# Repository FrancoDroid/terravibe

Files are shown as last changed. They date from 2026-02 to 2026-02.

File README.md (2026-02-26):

# Terra Vibe - Peneira Vibratória
No campo da arqueologia, muitos processos ainda dependem de ferramentas manuais que, embora eficientes, podem tornar o trabalho repetitivo, demorado e suscetível a variações humanas. A peneiração de sedimentos é um desses processos: essencial para identificar artefatos e microvestígios, mas frequentemente limitada por equipamentos improvisados ou difíceis de transportar.

Este projeto nasceu da necessidade de criar uma solução acessível, portátil e replicável para equipes de campo e laboratórios: uma peneira vibratória open source, com componentes de baixo custo. O objetivo é acelerar o processo, reduzir o esforço físico, melhorar a eficiência da triagem e aumentar a confiabilidade dos resultados.

A proposta permite que qualquer grupo possa construir, adaptar ou otimizar o equipamento de acordo com suas necessidades específicas. Ao tornar o projeto open source, pretendemos facilitar a colaboração entre arqueólogos, pesquisadores e desenvolvedores, promovendo melhorias contínuas e ampliando o acesso a ferramentas profissionais de peneiração.

Gemini_Generated_Image_eo8nz3eo8nz3eo8n

## Fatores Principais

- Completamente gratuito e open source
- Estrutura fixa e resistente a base de canos PVC
- Não requer microcontroladores ou hardwares caros
- Possui ajuste de velocidade de peneiração para agilidade ou para fragmentos mais fragéis.
- Componentes acessíveis e fáceis de obter
- Não requer instalação de software/circuitos elaborados
- Funcionamento requer apenas uma tomada de 110v

## Como Funciona?

O processo é simples: o usuário distribui o material a ser peneirado (solo, sedimentos ou fragmentos arqueológicos) sobre a superfície da peneira, garantindo que esteja espalhado de forma uniforme. Logo abaixo da peneira, posiciona-se um recipiente de coleta, como um balde ou bandeja, que irá receber a terra, areia ou outros materiais indesejados que passarem pela malha durante o processo. Em seguida, com o TerraVibe ligado a tomada, basta ajustar o potenciômetro para definir a intensidade de vibração desejada. Essa vibração facilita a separação natural dos fragmentos: pedaços maiores (como artefatos, fragmentos cerâmicos ou pequenas estruturas) permanecem sobre a peneira para análise enquanto, os materiais indesejados caem para o recipiente de coleta através da malha.

## Lista de Materiais

| Componente                              | Quantidade | Preço Unidade (R$) | Preço (R$) |
|-----------------------------------------|------------|----------------------|------------|
| Joelho 90 PVC 25mm                      | 4          | 0,58                 | 2,32       |
| Tê PVC 25mm                             | 6          | 0,99                 | 3,96       |
| Luva PVC 25mm                           | 1          | 0,64                 | 0,64       |
| Conexão Tubo Curva 3 Saídas PVC 25 mm   | 4          | 6,29                 | 25,16      |
| Peneira 60x40cm                         | 1          | 59,90                | 59,90      |
| Molas de Tração                         | 4          | 9,50                 | 38,00      |
| Corda Elástica com Gancho               | 1          | 21,13                | 21,13      |
| Cano PVC 20mm (3 metros)                | 3          | 9,50                 | 28,50      |
| Cano PVC 20mm (1 metro)                 | 1          | 5,65                 | 5,65       |
| Cabo Elétrico 1 metro 1,5mm²            | 1          | 3,23                 | 3,23       |
| Controlador p/ Motor                    | 1          | 17,52                | 17,52      |
| Motor                                   | 1          | 42,95                | 42,95      |
| Fonte Bivolt 12V 50A DC                 | 1          | 96,45                | 96,45      |
| Cabo Extensor Acendedor                 | 1          | 2,66                 | 2,66       |
| Fusível 15A 250V                        | 1          | 0,97                 | 0,97       |
| Plugue de tomada (2 pinos)              | 1          | 2,89                 | 2,89       |
| Total                                   | —          | —                    | 351,93     |

## Manual de Montagem

Nós montamos o nosso TerraVibe de uma forma e documentamos ela em um guia de montagem com o passo-a-passo para produção. A baixo, temos o link do manual.

(https://github.com/FrancoDroid/terravibe/blob/main/Manual%20de%20Montagem%20-%20TerraVibe.pdf)
## Imagem da TerraVibe

A TerraVibe é a nossa solução portátil em cano de PVC. A estrutura é leve e a peneira tem 30 por 60 centímetros. O sistema usa um motor alimentado por fonte e controlado por um potênciometro que permite ajustar a intensidade da vibração. Isso garante que a terra seja separada sem danificar os artefatos. 

Foto de Miguel López

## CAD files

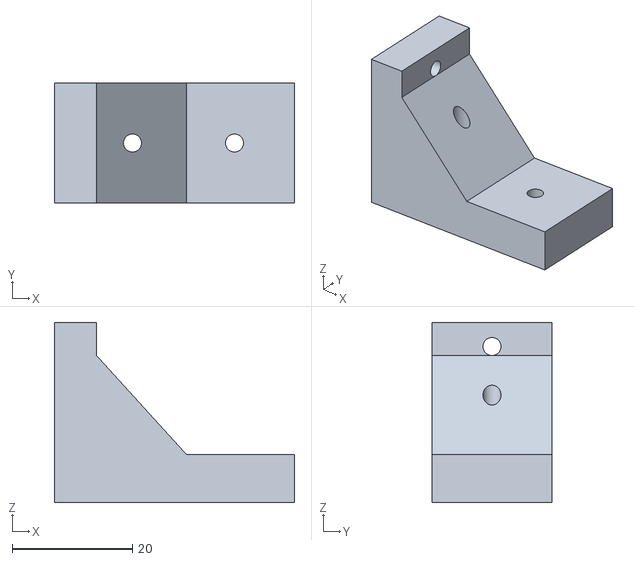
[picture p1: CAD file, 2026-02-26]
Peças para Impressão 3D/cantoneira peneira 2.STL
40.0 x 20.0 x 30.0

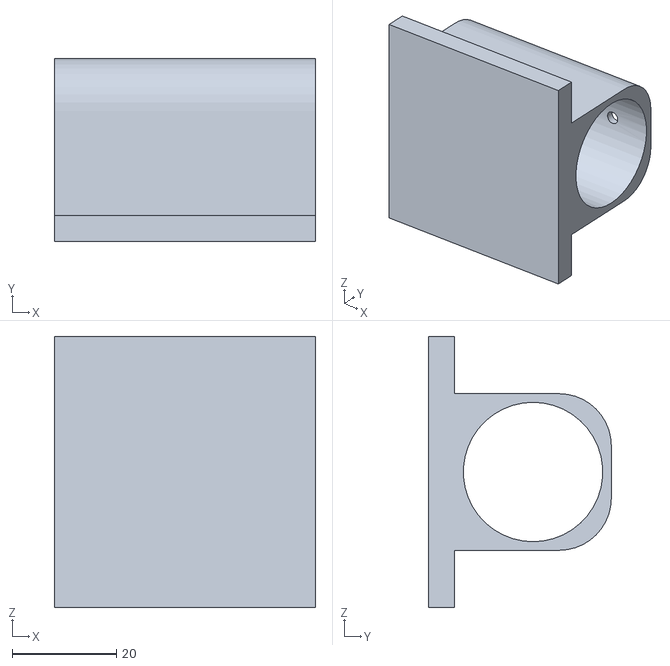
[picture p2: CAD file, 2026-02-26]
Peças para Impressão 3D/abraçadeira.STL
50.0 x 35.0 x 52.0

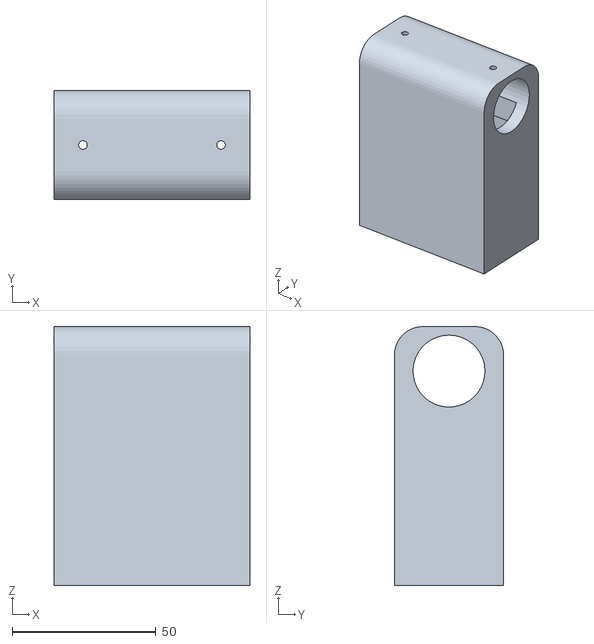
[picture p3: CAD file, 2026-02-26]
Peças para Impressão 3D/peca_potenciometro_para_imprimir.STL
68.0 x 38.0 x 90.0

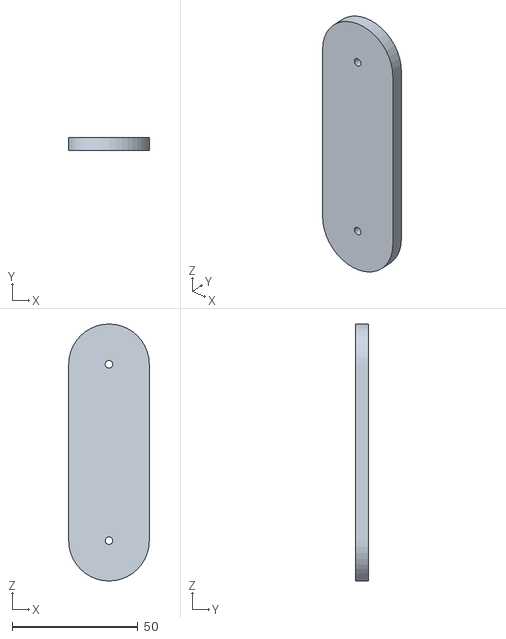
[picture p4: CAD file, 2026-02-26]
Peças para Impressão 3D/barra do pistao.STL
32.0 x 5.00 x 102.0

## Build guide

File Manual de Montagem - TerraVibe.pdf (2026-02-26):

### FRANCO DROID Manual de Montagem TerraVibe

Sumário

Rio de Janeiro
2026

### 0. Materiais

### 0.1 Estrutura (PVC)

- 3 canos de PVC de 3 metros
- 1 cano de PVC de 1 metro
- 4 joelhos de PVC 90°
- 6 conexões PVC tipo Tê
- 4 conexões PVC tipo curva com 3 saídas
- Parafusos pequenos
- Fita isolante

### 0.2 Ferramentas

- Serra para PVC
- Furadeira
- Broca de 4,5 mm
- Micro-retífica (ou furadeira para recortes)
- Régua ou fita métrica
- Lápis ou marcador

### 0.3 Sistema Elétrico

- Fonte de alimentação DC
- Motor DC vibratório
- Controlador de velocidade com potenciômetro
- Plugue macho de tomada
- Cabo elétrico (1,5 mm² ou 2,5 mm²)
- Cabo extensor tipo acendedor automotivo
- Fusível de 15 A

### 1. Preparação dos canos

### 1.1 Cortes Iniciais

Cano 1 (3 metros)
Faça marcações para corte nas seguintes medidas:
- 64 cm
- 128 cm
- 146 cm
- 164 cm
- 182 cm
- 200 cm

- 231 cm
- 262 cm
- 293 cm

Cano 2 (3 metros)
Faça marcações para corte nas seguintes medidas:
- 70 cm
- 140 cm
- 210 cm
- 280 cm

Cano 3 (3 metros)
Faça marcações para corte nas seguintes medidas:
- 66 cm
- 132 cm
- 198 cm
- 264 cm
- 295 cm

Cano 4 (1 metro)
Faça uma marcação para corte em:
- 87 cm

Após os cortes você terá:
- 2 canos de 64 cm
- 4 canos de 70 cm
- 4 canos de 31 cm
- 4 canos de 18 cm
- 1 cano de 87 cm
- 4 canos de 66 cm

### 1.2 Furos

Selecione dois canos de 66 cm (aleatoriamente). Faça furos de 4,5 mm:
- A 2 cm de cada extremidade
- Alinhados entre si

### 1.3 Encaixe do Potenciômetro

Pegue um dos canos de 66 cm já furados.

Faça uma marcação retangular:
- 25 mm × 15 mm
- A 32 cm das extremidades
Depois faça o corte com furadeira ou micro-retífica. Esse espaço será usado para instalar o potenciômetro.

### 1.4 Saída dos Cabos

Pegue um cano de 31 cm.
Faça uma marcação:
- 25 mm × 15 mm
- A 5 cm de uma extremidade
Depois faça o corte.
Esse espaço será utilizado para passagem dos cabos elétricos.

### 2. Estrutura

### 2.1 Quadrado 1

Comece pegando um cano de 64 cm e coloque um joelho de 90° em cada extremidade.

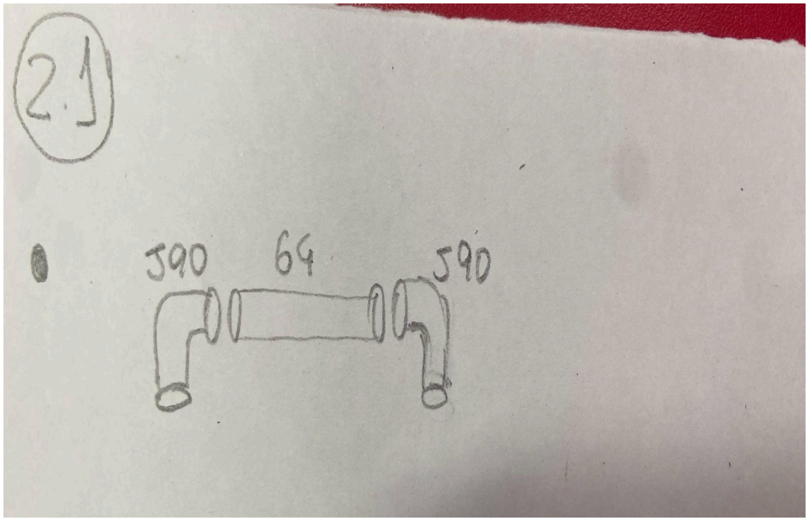
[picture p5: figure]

Encaixe nas pontas sobressalentes dos joelhos de 90º um cano de 18 cm.

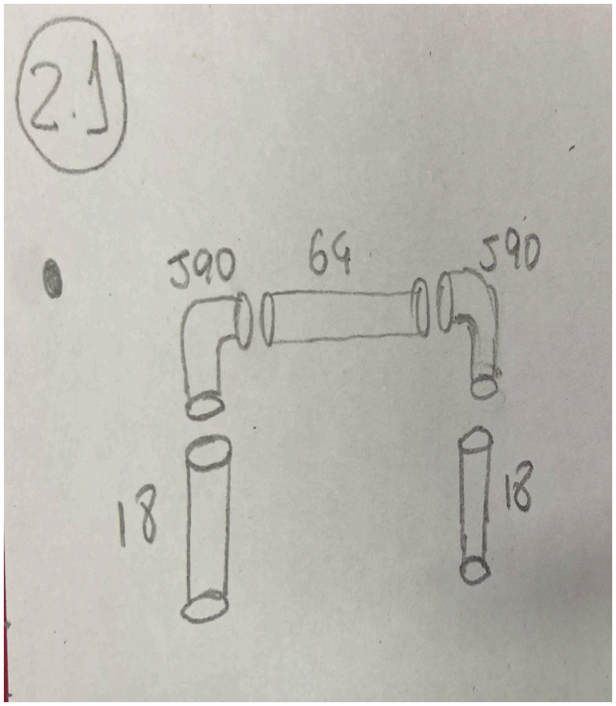
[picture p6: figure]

Coloque um tê encaixado no eixo horizontal na ponta de cada cano de 18 cm. Em seguida, encaixe um cano de 70 cm na outra ponta do tê.

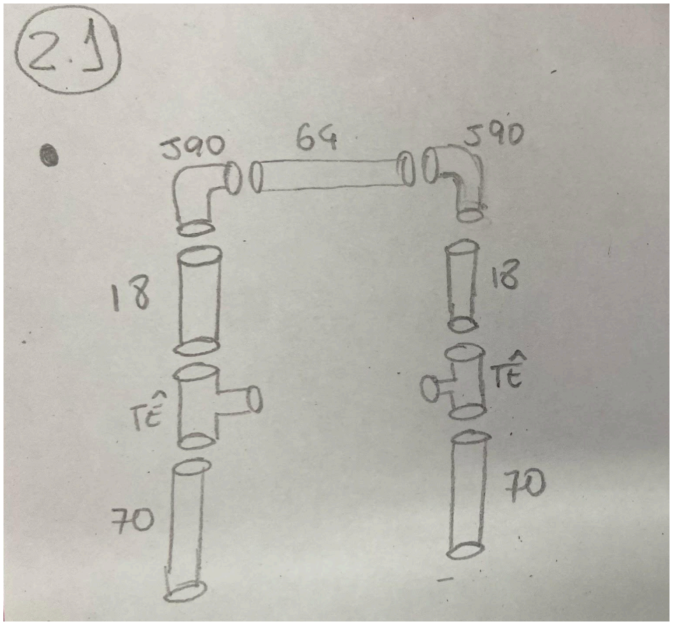
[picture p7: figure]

Na ponta do cano de 70 cm, coloque outro joelho de 90º, a seguir pegue o segundo cano de 64 cm e encaixe-o entre os dois joelhos de baixo.

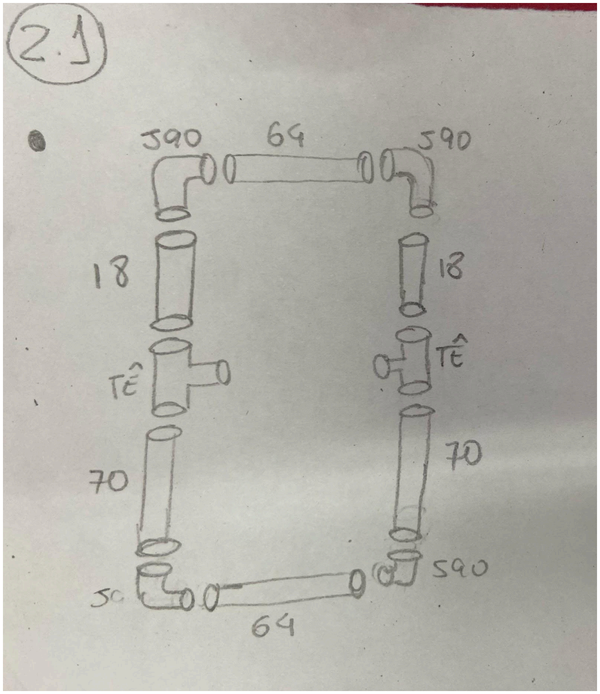
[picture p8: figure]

### 2.2 Quadrado 2

Pegue um tê, encaixe dois canos de 31 cm no eixo horizontal e coloque dois joelhos 90, um em cada ponta.
Repita o processo com os outros dois canos de 31 cm, mas substitua os joelhos por conexões curvas com 3 saídas

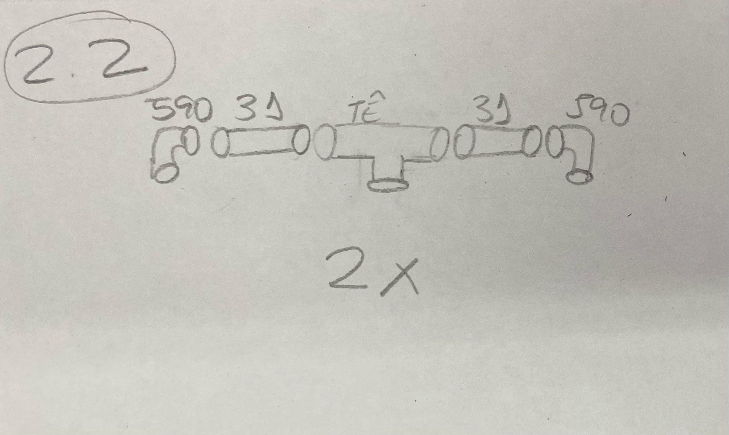
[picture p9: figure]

Na estrutura sem furo anexe dois canos de 18 cm em cada ponta dos joelhos.

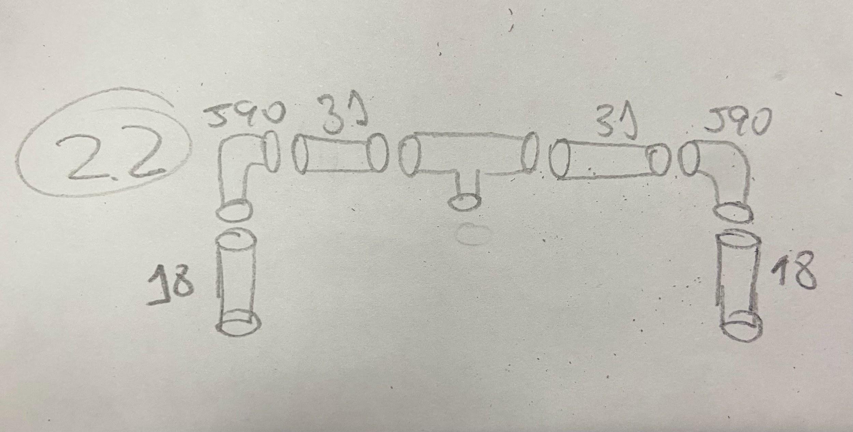
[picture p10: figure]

Na estrutura com furo, encaixe dois canos de 70 cm nas pontas das conexões curvas de 3 saídas.

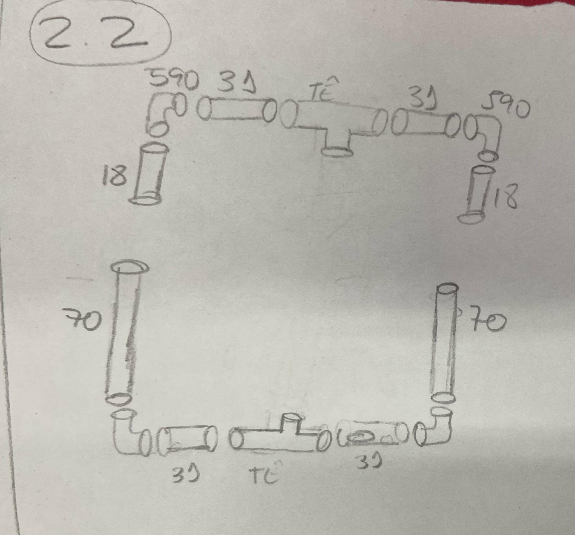
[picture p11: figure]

Conecte as duas estruturas com o eixos verticais dos dois através do cano de 87 cm.

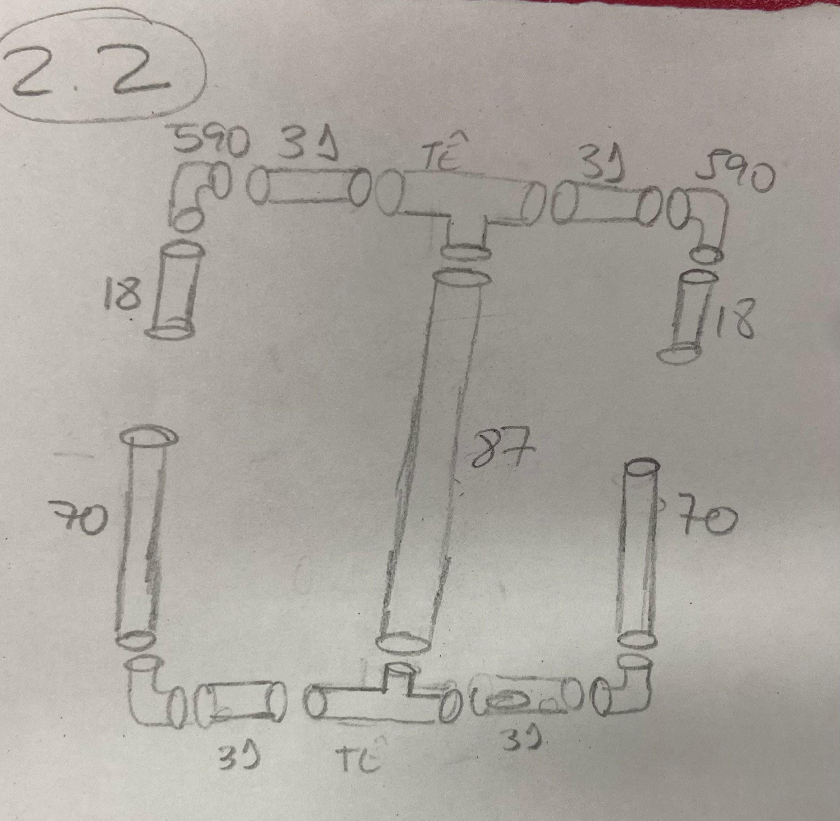
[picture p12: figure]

Nas pontas sobressalentes dos canos de 18 cm e 70 cm encaixe um tê no eixo horizontal. Repita esse mesmo processo do outro lado.

### 2.3 Formação do Paralelepípedo

Pegue os dois quadriláteros formados nos passos anteriores e conecte-os encaixando os canos de 66 cm nos furos nos tês.
Pegue os outros dois canos de 66 cm e encaixe-os nos conectores de 3, juntando as partes de baixo dos quadriláteros.
Repita os mesmos processos do outro lado.

### 3. Fonte

### 3.1 Plugue da Tomada

Desparafuse o plugue macho e corte dois pedaços de cabo que serão usados para ligar a fonte à tomada. O comprimento desses cabos depende da distância entre a fonte e a tomada. No nosso caso, utilizamos 25 cm.

OBS: Use sempre um cabo adequado e seguro para esse tipo de ligação. O recomendado é 1,5 mm², mas, se preferir algo ainda mais robusto, pode usar 2,5 mm² sem problemas.

Depois de cortar o cabo:
Encaixe as pontas no plugue macho e aperte os parafusos para fixá-las.

Conecte a outra extremidade na entrada AC da fonte. Basta desparafusar os terminais da fonte, inserir os fios e apertar novamente.
Como a entrada é corrente alternada (AC), a posição dos fios não altera o funcionamento.

OBS: Após realizar qualquer conexão, isole bem as junções com fita isolante para evitar curto-circuitos e garantir maior segurança ao funcionamento do sistema.

Como a entrada é corrente alternada (AC), a posição dos fios não altera o funcionamento. Os terminais marcados como:
- N → Neutro

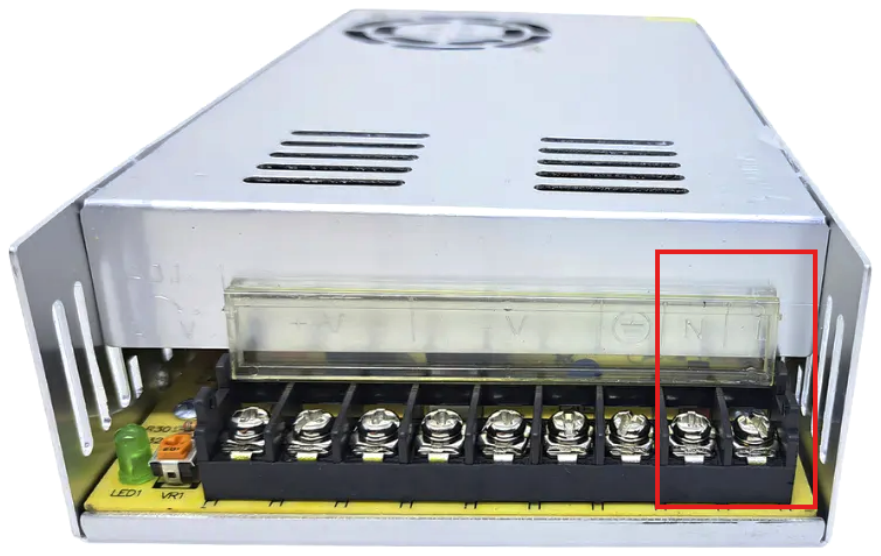
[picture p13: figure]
● L → Fase

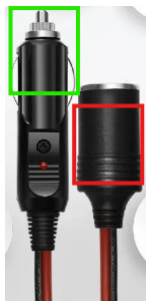
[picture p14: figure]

### 3.2 Segurança

Corte o Cabo Extensor de Acendedor em duas partes iguais:

1 - Fêmea (Vermelho)
2 - Macho (Verde)

A parte fêmea será conectada diretamente à saída da fonte. Siga a polaridade correta:

Fio vermelho = positivo (V+)
Fio preto = negativo (V–)

Essa será a extremidade que receberá a energia da fonte.

A parte macho possui um porta-fusível embutido. Ele serve como proteção: caso ocorra um problema de corrente, o fusível queimarará primeiro, interrompendo o circuito de forma segura.

Para acessar o fusível:
1. Desrosqueie a ponta.
2. Retire o fusível original de 10 A.
3. Substitua por um fusível de 15 A (que é o valor adequado para o projeto).

Quando você conectar o plugue macho na parte fêmea, o circuito entre a fonte e o equipamento se fecha, permitindo a passagem de corrente somente através da proteção do fusível.

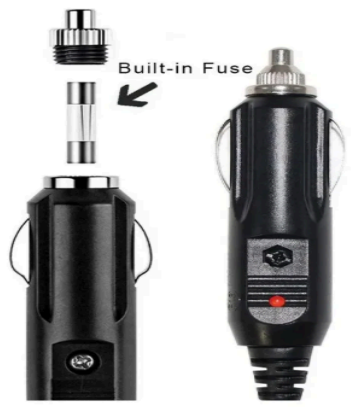
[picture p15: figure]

### 4. Motor

### 4.1 Controlador (Potenciômetro)

Para energizar o motor, o primeiro passo é conectar os cabos do plugue macho ao controlador. O fio vermelho deve ser ligado ao terminal B+ e o fio preto ao terminal B-. Basta desparafusar os terminais do controlador, inserir os fios e apertá-los novamente para garantir uma conexão firme.
- Vermelho → B+
- Preto → B–

Em seguida, corte dois cabos de aproximadamente 20 cm cada; eles serão responsáveis por levar a energia do controlador até o motor. Conecte um desses cabos ao terminal M+ e o outro ao terminal M-, seguindo o mesmo procedimento: desparafuse, encaixe o fio e parafuse novamente.

Depois disso, ligue as pontas opostas desses cabos diretamente aos terminais do motor, mantendo a polaridade, o cabo vindo do M+ deve ir para o positivo do motor, e o cabo do M-deve ir para o negativo.
- M+ → positivo do motor
- M– → negativo do motor

Após realizar essas conexões, isole bem as junções com fita isolante para evitar curto-circuitos e garantir maior segurança ao funcionamento do sistema.

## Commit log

2026-02-26 Modelo das peças de impressão 3D
    Os arquivos em STL de todas as peças 3D usadas na Terravibe.
    [Encaixe da roda 2.STL, abraçadeira.STL, barra do pistao.STL, peca_potenciometro_para_imprimir.STL]
2026-02-26 Create Peças para Impressão 3D
2026-02-26 Update Peças para Impressão 3D
2026-02-27 Rename Manual de Montagem - TerraVibe (1).pdf to Manual de Montagem - TerraVibe.pdf
2026-02-27 Rename Manual de Montagem - TerraVibe (1).pdf to Manual de Montagem - TerraVibe .pdf
2026-02-27 Rename Manual de Montagem - TerraVibe .pdf to Manual de Montagem - TerraVibe.pdf
